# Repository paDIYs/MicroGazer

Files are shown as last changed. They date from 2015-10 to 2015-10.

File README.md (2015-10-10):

# MicroGazer

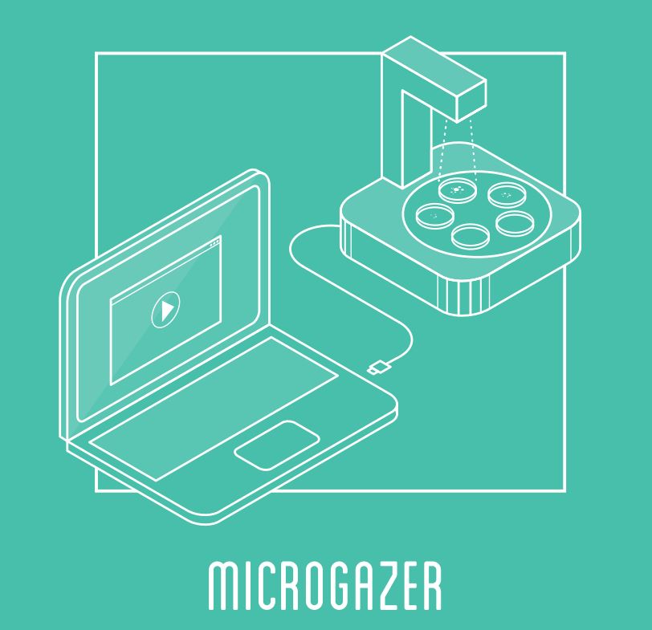
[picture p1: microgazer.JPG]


The “Micro-Gazer” is an innovative tool developed by the BioHacker Experience in collaboration with the FabLabTO: it is an automatic station for visualizing and analyzing the microbial growth on Petri Dish inoculated with the "Microbiome of a Maker" [learne more](http://biohackingexperience.tumblr.com/).

The MicroGazer is equipped with a backlit rotating plate, that can host up to 5 Petri dishes, and a capture position with a camera. It is controlled by an Arduino Yun board that manages the camera and the motor that moves the rotating plate. The images acquired by the camera are stored on the memory of the Arduino board and, if connected to the internet, uploaded to the cloud.  Thus, the images document the growth of the bacteria colonies and they can be used to create a time-lapse video that highlight the complexity (the dimensions and directions) of bacteria proliferation.

## Procedure
* STEP1: The Petri Dishes are prepared with culture medium without any type of antibiotics.

* STEP2: The Maker can inoculate the Petri dish by touching the medium surface with her/his skin, breathing on it or using a buccal swab.

* STEP3: The inoculated Petri dish is placed on the MicroGazer. It could host up to 5 Petri Dish for simultaneously and comparable incubations.

* STEP4: The MicroGazer incubate the Petri Dishes and periodically capture a photograph of each Petri dish, documenting the bacteria growth.

## Recipe & Experiment Description
##### Home Made DIY Solid Culture Media
* 10g table salt to provides ions for transport and osmotic balance

* 5g dried yeast for bread preparation to provide a plethora of organic compounds helpful for bacterial growth

* 3g sugar as a nutrient  to help bacterial growth

* 15g Agar- Agar, a vegetarian gelatin substitute produced from a variety of seaweed vegetation which is sold in health food stores. It is used to provide a solid medium for microorganisms growth.

Dissolve components in 1 liter of distilled water.  Put into a glass bottle and sterilize by boiling in a water bath  for 30 minutes.

Fill the Petri dish with agar medium and use the top half of the Petri dish to cover the bottom portion and allow the solution to cool and harden for at least an hour.

Inoculate the plate with your finger print or your mouth cotton swap.

Place the plates in a warm place ( 25°-37°C), in 12 hs you’ll start to see microorganisms growing into your plate and you’ll continue to see more and larger colonies for the next days.

#### Team
Stefano Paradiso, Valentina Margaria, Riccardo Castagna, Irio Lavagno, Alessandro Argenio

## BOM
* Arduino Yun
* Stepper motor NEMA 17
* Voltage regulator 5 volt [L7800](http://cdn.sparkfun.com/datasheets/Components/General/TO-220.pdf)
* H bridge [SN754410](https://www.sparkfun.com/datasheets/IC/SN754410.pdf)
* UVC compatible USB webcam [List](https://en.wikipedia.org/wiki/List_of_USB_video_class_devices)
* Power supply 12V
* 20cm of streep led
* 4mm plywood 100 x 60cm
* 4mm plexiglass 50 x 25cm
* n.12 bolts and nuts M3 16mm
* n.3 Balls casters

## Software configuration

##### UVC driver and webcam software
update the software list:

    opkg update

install UVC drivers:

    opkg install kmod-video-uvc

we will also need the python-openssl:

    opkg install python-openssl

install the webcam software:

    opkg install fswebcam

##### Dropbox API

We must create un APP on our Dropbox account [https://www.dropbox.com/developers](https://www.dropbox.com/developers)
Now we will use pip to intall the Dropbox SDk

    opkg update
    opkg install distribute
    easy_install pip
    pip install dropbox

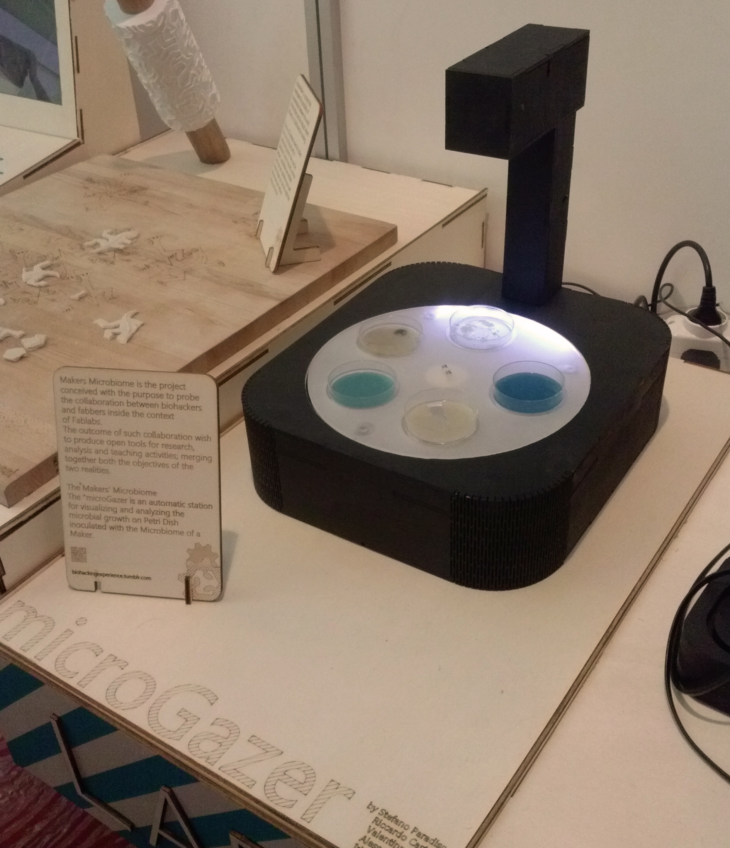
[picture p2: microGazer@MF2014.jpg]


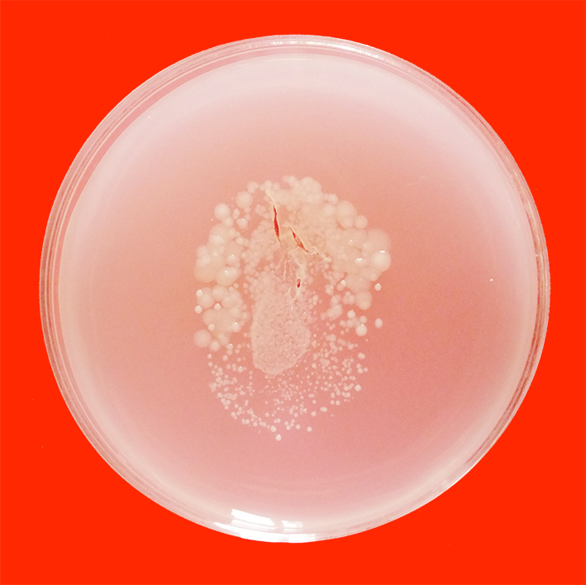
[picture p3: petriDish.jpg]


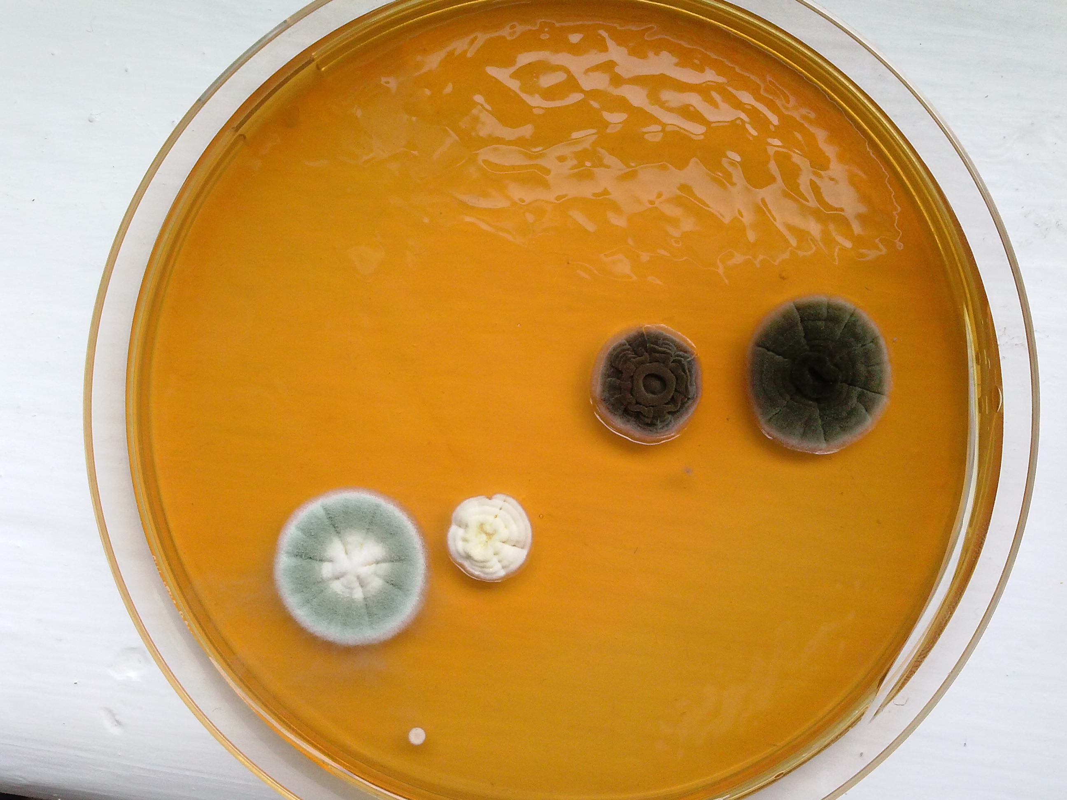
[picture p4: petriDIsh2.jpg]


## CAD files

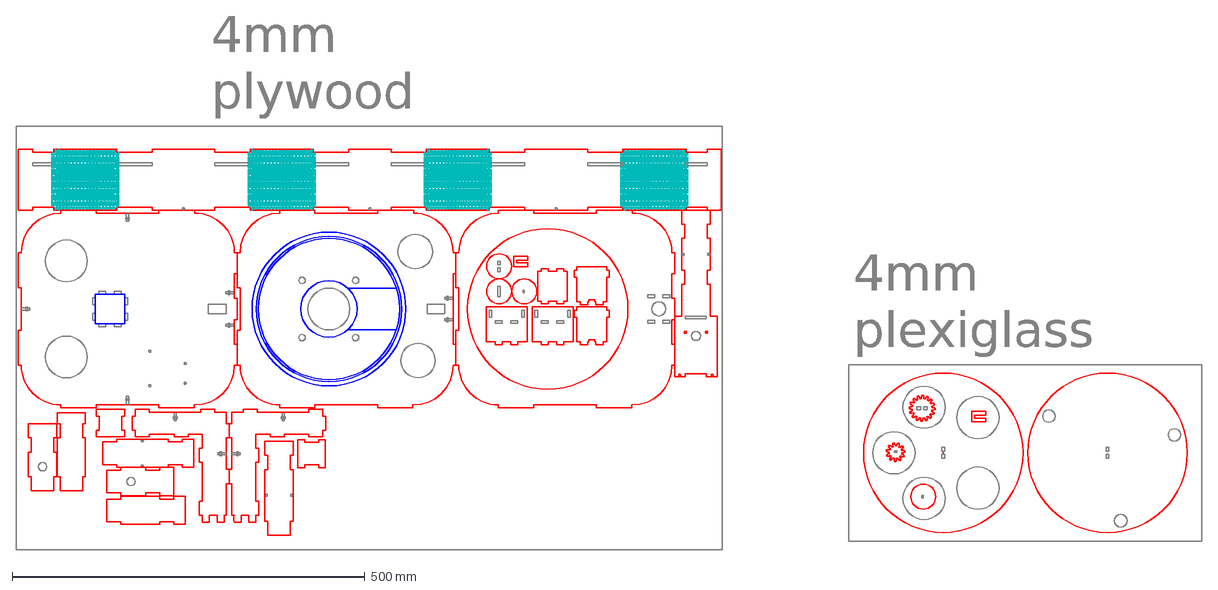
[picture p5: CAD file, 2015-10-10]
caseCuttingFile.dxf
4mm plexiglass
4mm plywood

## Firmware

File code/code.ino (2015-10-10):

//include library
#include <passopasso.ino>
#include <Bridge.h>
#include <Process.h>

//define stepperMotor pin
int DIR_A = 12;
int STP_A = 3;
int DIR_B = 13;
int STP_B = 11;


void setup() {
  Bridge.begin();
  //Serial.begin(9600);
  pinMode(DIR_A, OUTPUT);
  pinMode(DIR_B, OUTPUT);
  pinMode(STP_A, OUTPUT);
  pinMode(STP_B, OUTPUT);
}


void loop() {
  Process p;
  //rotate to 1st Petri Dish
  for (int x = 0; x < 7; x++) {
    passoIn(20);
  }
  //take a photo
  p.runShellCommand("python /mnt/sda1/arduino/www/dpbcam.py 'a'");
  while (p.running());
  delay(3000);

  //rotate to 2nd Petri Dish
  for (int x = 0; x < 9; x++) {
    passoIn(20);
  }
  //take a photo
  p.runShellCommand("python /mnt/sda1/arduino/www/dpbcam.py 'b'");
  while (p.running());
  delay(3000);

  //rotate to 3rd Petri Dish
  for (int x = 0; x < 9; x++) {
    passoIn(20);
  }
  //take a photo
  p.runShellCommand("python /mnt/sda1/arduino/www/dpbcam.py 'c'");
  while (p.running());
  delay(3000);

  //rotate to 4th Petri Dish
  for (int x = 0; x < 9; x++) {
    passoIn(20);
  }
  //take a photo
  p.runShellCommand("python /mnt/sda1/arduino/www/dpbcam.py 'd'");
  while (p.running());
  delay(3000);

  //rotate to 5th Petri Dish
  for (int x = 0; x < 9; x++) {
    passoIn(20);
  }
  //take a photo
  p.runShellCommand("python /mnt/sda1/arduino/www/dpbcam.py 'e'");
  while (p.running());
  passoOff(3000);

  //stop 15 minute
  for (int x = 0; x < 7; x++) {
    passoIn(20);
  }
  delay(1000);
  passoOff(2000);
  delay(900000);
}
